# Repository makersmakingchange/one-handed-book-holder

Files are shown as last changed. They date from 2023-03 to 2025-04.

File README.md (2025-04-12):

<!--  Open Source Assistive Technology: GitHub Readme Template -->
<!-- Template files available at https://github.com/makersmakingchange/OpenAT-Template -->

<!-- TITLE -->
# One Handed Book Holder

<!-- SUMMARY -->
The One Handed Book Holder is an inexpensive 3D printed device that makes it easier to hold the pages of a book open with only one hand. Users with limited hand dexterity or use of only one hand my find this device beneficial.  

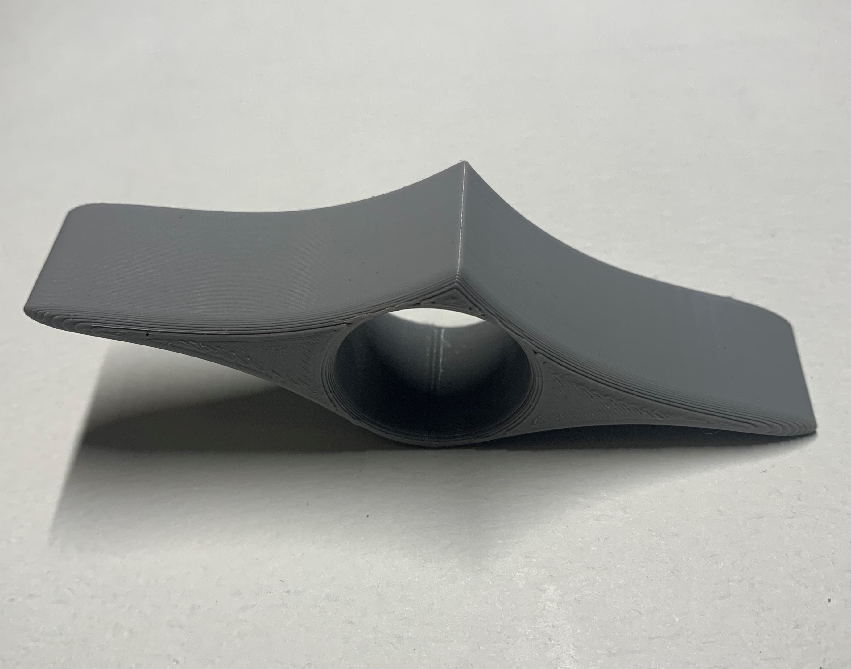
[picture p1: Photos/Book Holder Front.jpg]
The front view of a grey 3D printed handheld book holder


## Makers Making Change Assistive Device Library
 - https://www.makersmakingchange.com/s/product/one-handed-book-holder/01tJR00000092SPYAY

## How to Obtain a One Handed Book Holder
### 1. Do it Yourself (DIY) or Do it Together (DIT)

This is an open-source assistive technology, so anyone is free to build it. All of the files and instructions required to build a One Handed Book Holder are contained within this repository. Refer to the Maker Checklist below.

### 2. Request a build of this device

If you would like to obtain a One Handed Book Holder, you may submit a build request through the [MMC Library Page](https://makersmakingchange.com/project/one-handed-book-holder/). The requestor is responsible for the cost of materials and any shipping.

### 3. How to build this device for someone else

If you have the skills and equipment to build this device, and would like to donate your time to create this device for someone who needs it, visit the [MMC Maker Wanted](https://makersmakingchange.com/maker-wanted/) section.

## Getting Started

### 1. Print the 3D Printable components

All of the files and individual print files can be in the [/Build_Files/3D_Printing_Files](/Build_Files/3D_Printing_Files/) folder.

## Files
This section includes all the information and files required to build and modify the device, including documentation, design files, and build files. 

### Documentation
<!-- DOCUMENTATION -->
| Document | Version | Link |
|----------|---------|------|
| Design Rationale     | 1.0 | [One_Handed_Book_Holder_Design_Rationale](/Documentation/One_Handed_Book_Holder_Design_Rationale.pdf) |
| Bill of Materials    | 1.0 | [One_Handed_Book_Holder_BOM](/Documentation/One_Handed_Book_Holder_BOM.xlsx) |
| Assembly Guide       | N/A | No Assembly Required
| Maker Checklist      | 1.0 | [One_Handed_Book_Holder_Checklist](/Documentation/One_Handed_Book_Holder_Maker_Checklist.pdf) |
| User Guide           | 1.0 | [One_Handed_Book_Holder](/Documentation/One_Handed_Book_Holder_User_Guide.pdf)           |
| Changelog            | 1.0 | [One_Handed_Book_Holder_Changelog](/Documentation/One_Handed_Book_Holder_Changelog.pdf)               |

### Design Files
<!-- DESIGN FILES -->
- Not available 

### Build Files
<!-- BUILD FILES -->
 - [3D Printing Files](/Build_Files/3D_Printing_Files)

## License
<!-- LICENSE -->
Everything needed or used to design, make, test, or prepare the One Handed Book Holder is licensed under the CERN 2.0 Permissive license <https://ohwr.org/project/cernohl/wikis/Documents/CERN-OHL-version-2> (CERN-OHL-P).

Accompanying material such as instruction manuals, videos, and other copyrightable works that are useful but not necessary to design, make, test, or prepare the One Handed Book Holder are published under a Creative Commons Attribution-ShareAlike 4.0 license <https://creativecommons.org/licenses/by-sa/4.0/> (CC BY-SA 4.0).

## Attribution
<!-- ATTRIBUTION -->
 - Design by [Mathis](https://www.myminifactory.com/users/mgigli) and posted on [MyMiniFactory](https://www.myminifactory.com/object/3d-print-one-hand-book-holder-41414)
 - Documentation by Makers Making Change
 - The documentation template was created by Makers Making Change and is used under a CC BY-SA 4.0 license. It is available at the following link: https://github.com/makersmakingchange/OpenAT-Template

----

<!-- ABOUT MMC START -->
## About Makers Making Change
[Makers Making Change Logo](https://www.makersmakingchange.com/)

Makers Making Change is a program of [Neil Squire](https://www.neilsquire.ca/), a Canadian non-profit that uses technology, knowledge, and passion to empower people with disabilities.

Makers Making Change leverages the capacity of community based Makers, Disability Professionals and Volunteers to develop and deliver affordable Open Source Assistive Technologies.

 - Website: [www.MakersMakingChange.com](https://www.makersmakingchange.com/)
 - GitHub: [makersmakingchange](https://github.com/makersmakingchange)
 - Bluesky: [@makersmakingchange.bsky.social](https://bsky.app/profile/makersmakingchange.bsky.social)
 - Instagram: [@makersmakingchange](https://www.instagram.com/makersmakingchange)
 - Facebook: [makersmakechange](https://www.facebook.com/makersmakechange)
 - LinkedIn: [Neil Squire Society](https://www.linkedin.com/company/neil-squire-society/)
 - Thingiverse: [makersmakingchange](https://www.thingiverse.com/makersmakingchange/about)
 - Printables: [MakersMakingChange](https://www.printables.com/@MakersMakingChange)

### Contact Us
For technical questions, to get involved, or to share your experience we encourage you to [visit our website](https://www.makersmakingchange.com/) or [contact us](https://www.makersmakingchange.com/s/contact).
<!-- ABOUT MMC END -->

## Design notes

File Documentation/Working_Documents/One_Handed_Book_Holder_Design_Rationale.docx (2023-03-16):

# Introduction

The One Handed Book Holder is an inexpensive 3D printed device that makes it easier to hold the pages of a book open with only one hand. Users with limited hand dexterity or use of only one hand my find this device beneficial.

# Research

## Commercial Designs

Title | Picture | Cost | Notes:

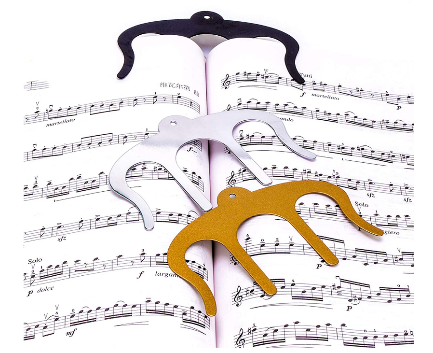
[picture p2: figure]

Music Book Clip (https://www.amazon.ca/Music-Book-Clips-Metal-Holders-Reading/dp/B07TCGN5NL?cv_ct_cx=page+holder&sbo=RZvfv%2F%2FHxDF%2BO5021pAnSA%3D%3D) | | $10 - $20 | This clip can be placed between the pages of a book to keep it open while reading. Typically used for sheet music, cooking books or other books are held on the same page for extended periods of time.

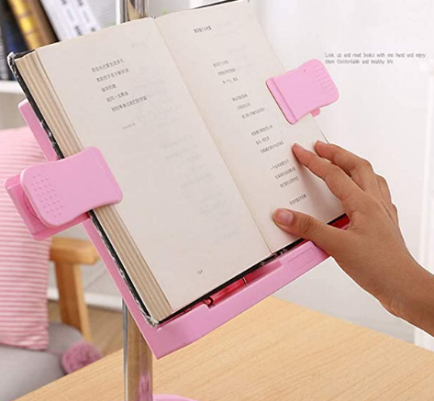
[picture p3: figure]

Adjustable Book Holder (https://www.amazon.ca/Adjustable-Multi-Function-One-Handed-Childrens-Artifact/dp/B08NYQLSL6) | | ~$80 | A stand that holds the pages of a book open with clips on either side. Reading height and angle can be adjusted.

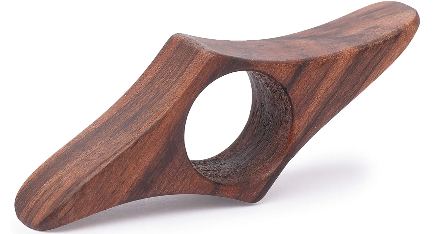
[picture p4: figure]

Book Page Holder (https://www.amazon.ca/TILISMA-Book-Page-Holder-Accessories/dp/B07PGW7C8R?cv_ct_cx=page+holder&sbo=RZvfv%2F%2FHxDF%2BO5021pAnSA%3D%3D) | | $10 - $20 | This device is placed on the user’s thumb to spread apart the pages of a book while actively reading. As it’s not fastened to the book, pages can still be turned easily.

DIY Designs

Title | Picture | Designer

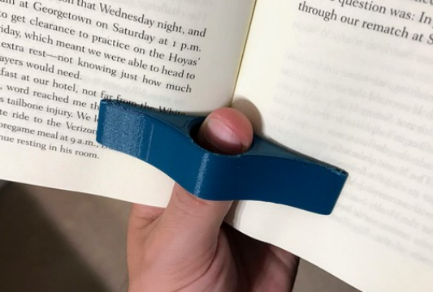
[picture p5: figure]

One Handed Book Holder (https://www.myminifactory.com/object/3d-print-one-hand-book-holder-41414) (Test 1) | | Mathis (https://www.myminifactory.com/users/mgigli)

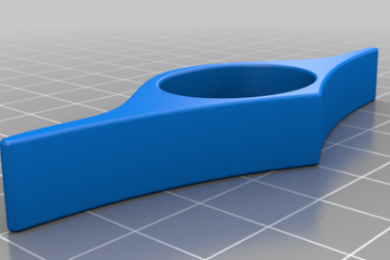
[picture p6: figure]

Page Holder (https://www.thingiverse.com/thing:4832820) (Test 2) | | Myles Kreling (https://www.thingiverse.com/Bison_Soldier)

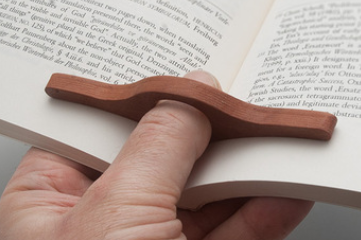
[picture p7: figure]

One Hand Book Holder (https://www.thingiverse.com/thing:2105202) (Test 3) | | Daniel Gross (https://www.thingiverse.com/ZenziWerken)

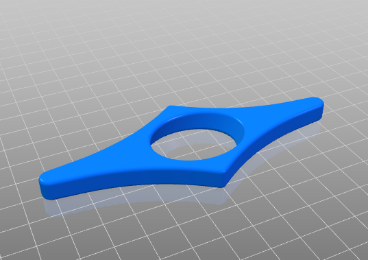
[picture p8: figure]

One Hand Book Holder V2 (https://www.thingiverse.com/thing:5257064) (Test 4) | | Peter Lunk (https://www.thingiverse.com/MrLunk)

# Requirements

## Goals

G01 | Must make it easier for users to hold a book open with one hand.
G02 | Must work or have options for right- and left-handed users.

## Functional Requirements

F01 | Must work for any standard sized book.
F02 | Must not damage or markup the pages of the book.
F03 | Must be comfortable for the user to use.

## Non-functional Requirement

NF01 | Should not require supports.

## Constraints

C01 | Must be printable using PLA
C02 | Must be printable using standard Maker 3D printers

# Existing Device Testing

## Test 1 – One Handed Book Holder (https://www.myminifactory.com/object/3d-print-one-hand-book-holder-41414)

License: MyMiniFactory - Credit - Remix - Noncommercial (https://www.myminifactory.com/object-licensing)

Mass: 7g

Print Time: 1h

### Print Testing

- Must be rotated 90o to print flat.

Initial Print:

- Did not print well
  - Fileted edges on the “arms” didn’t print too well.
  - Area around the thumb hole didn’t adhere to the print bed.

Second Print:

- Added adhesion brim.
- Printed very well and smooth.

### Functional Testing

- Fit nicely on the thumb.
- Good control over its position
- Did not mark the paper.
- Effective at holding the book pages open.

### Summary

This device worked very well when the print settings were adjusted. It effectively held the pages open and did not mark up the paper. It was the thickest holder considered which gave additional control over its position on the page.

## Test 2 – Page Holder (https://www.thingiverse.com/thing:4832820)

License: Attribution 4.0 International (CC BY 4.0)

Mass: 4g

Print Time: 30m

### Print Testing

- Printed very well.
- Surfaces are smooth.
- No supports or additional settings.

### Functional Testing

- Fit very nicely on the thumb.
- Easy to position.
- Arms were on the short side.
- Left marks on the page.

### Summary

This was the only device that had an oval thumb hole, making it fit and feel very nice. This also gave additional control over the positioning of the holder. However, it’s arms were quite short and had minimal rounding where they contacted the pages. This caused the device to leave marks on the paper.

## Test 3 – One Hand Book Holder (https://www.thingiverse.com/thing:2105202)

License: Attribution-NonCommercial-ShareAlike 4.0 International (CC BY-NC-SA 4.0)

Mass: 5g

Print Time: 38m

### Print Testing

- Printed very well.
- No supports or additional settings.

### Functional Testing

- Thumb hole is very small.
- Has long arms allowing It to effectively hold open the pages.
- No rounding making it uncomfortable and left marks on the paper.

### Summary

The original design was intended to laser cut out of wood. The thumb hole was quite small and the lack of edge rounding made it uncomfortable and left marks on the pages.

## Test 4 – One Hand Book Holder V2 (https://www.thingiverse.com/thing:5257064)

License: Attribution 4.0 International (CC BY 4.0)

Mass: 6g

Print Time: 44m

### Print Testing

- Printed very well.
- No supports of additional settings.

### Functional Testing

- Angled thumb hole so thumb can rest more naturally while reading.
- Thumb hole too large.
- Very hard to control and position.

### Summary

A few commons left on various other designs had requested an angled thumb hole to allow for an alternative grab. However, this large, angled thumb hole along with it being the thinnest considered, made this design very difficult to position on the page.

# Device Selection

Of the 4 designs considered, only the first one tested (Test 1 - One Handed Book Holder (https://www.myminifactory.com/object/3d-print-one-hand-book-holder-41414)) met every design requirement. After making some simple adjustments to the print orientation and settings, it effectively printed, felt comfortable to use, successfully held pages open and left no marks on the paper. For these reasons, we will proceed using this design for the final device.

# Opportunities for Improvement

- Adjustments to the fillets on the arms to increase the quality of the print.
- Refine the thickness of design to allow for adequate control while not covering too much of the page.

© 2023 by Neil Squire This work is licensed under the CC BY SA 4.0 License: http://creativecommons.org/licenses/by-sa/4.0 Files available at https://makersmakingchange.com/project/one-handed-book-holder Page 1 of 1

V1.0 | March 2023 One Handed Book Holder Design Rationale

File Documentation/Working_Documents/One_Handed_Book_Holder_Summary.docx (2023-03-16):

# Title

One Handed Book Holder

## Subtitle

An inexpensive 3D printed device that makes it easier to hold open a book.

## Device Specifications

Build Time:

< 1hr

1-4 hr

5-10hr

>10hr

Cost:

$0 - $10

$11 - $25

$26 - $50

$51 - $100

$101 - $250

$250+

Stage: Recently Added

Skills: 3D Printing

Need: Agility/Dexterity

Disability: Mobility / Physical

Difficulty: Beginner

License:

Usages: ADL, RL

Type:

Designer: Mathis (https://www.myminifactory.com/users/mgigli)

## Device Details

### Overview

The One Handed Book Holder is an inexpensive 3D printed device that makes it easier to hold the pages of a book open with only one hand. Users with limited hand dexterity or use of only one hand my find this device beneficial.

### Usage

To use this device, inset a thumb or finger into the finger hole. Slide the device between two pages of a book and rest the “pointed” side in the center crease. The arms of the device will hole the pages open while you read.

### Cost

This cost of filament to print this device is approximately $0.20.

#### Skills Required

This is a beginner level build that requires minimal 3D printing.

### Build Instructions

Refer to the 3D Printing Guide for detailed instructions.

#### Time Required

3D Printing Time: ~60min

Assembly Time: No assembly required.

#### Tools

- 3D Printer
- Fine grit sandpaper (Optional)

#### 3D Printing

1X One_Handed_Book_Holder.stl

### Attribution

Design by Mathis (https://www.myminifactory.com/users/mgigli) and posted on MyMiniFactory (https://www.myminifactory.com/object/3d-print-one-hand-book-holder-41414).

© 2023 by Neil Squire This work is licensed under the CC BY SA 4.0 License: http://creativecommons.org/licenses/by-sa/4.0 Files available at https://makersmakingchange.com/project/one-handed-book-holder Page 1 of 1

V1.0 | March 2023 One Handed Book Holder Summary

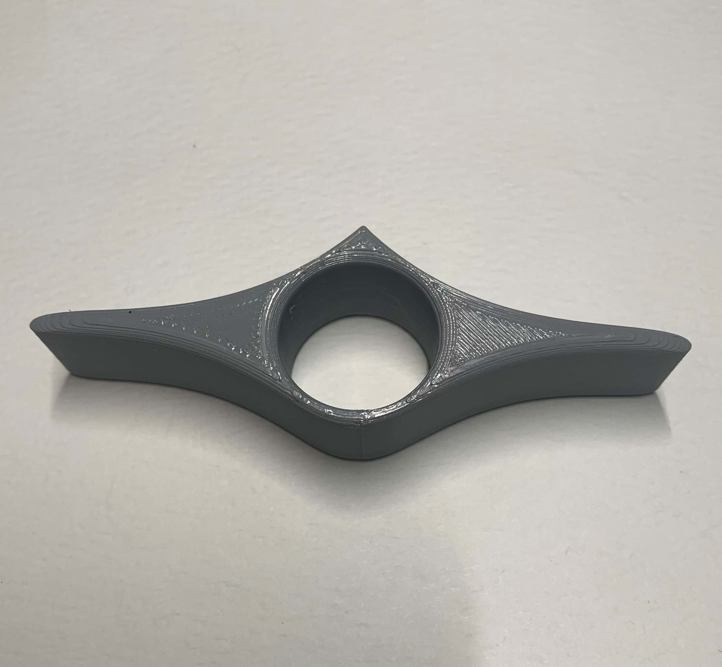
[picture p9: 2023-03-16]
Photos/Book Holder Top.jpg

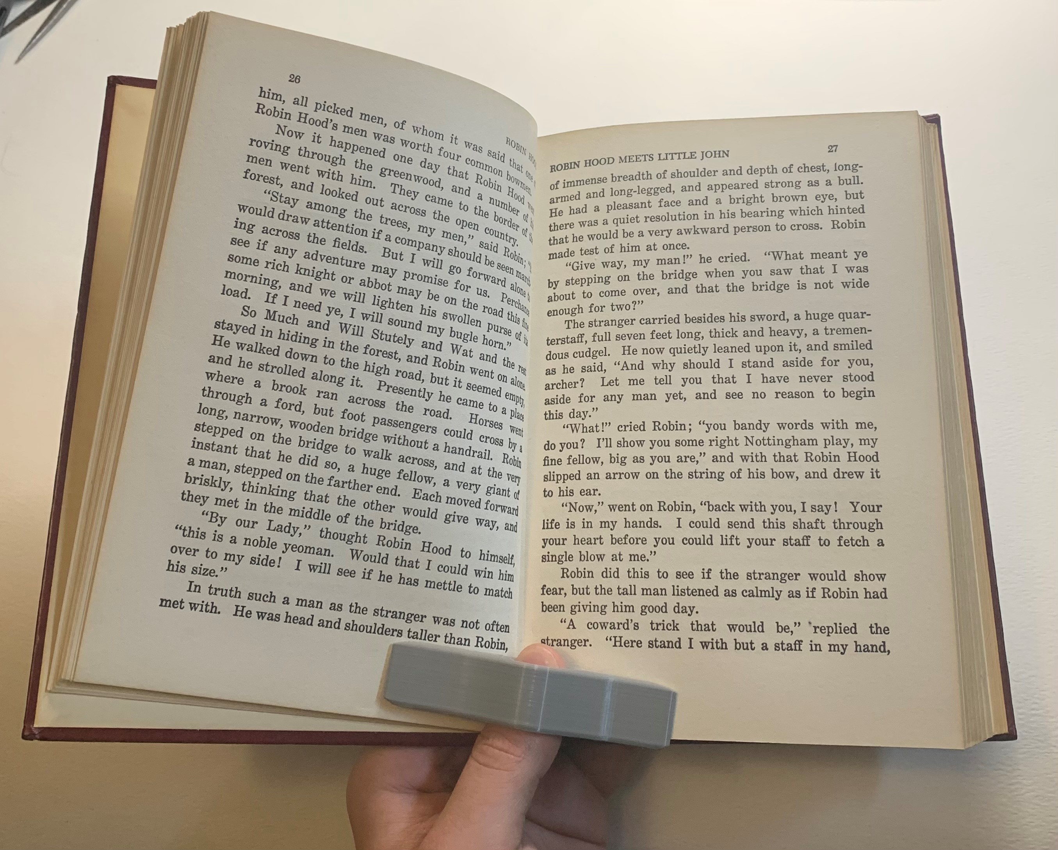
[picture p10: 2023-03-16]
Photos/Book Holder in use.jpg

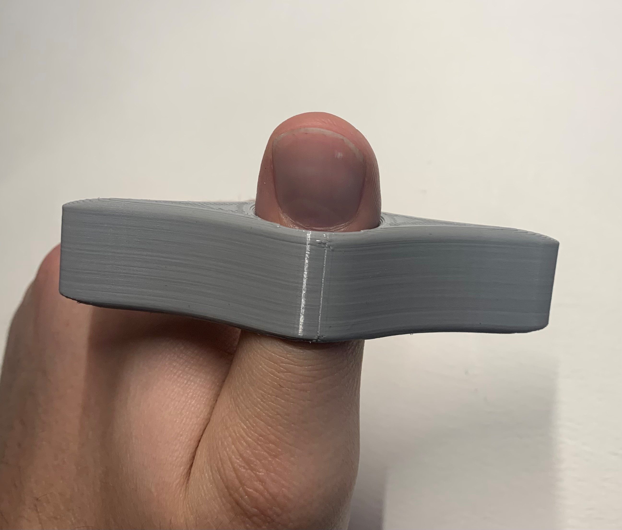
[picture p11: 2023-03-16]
Photos/Book Holder on thumb.jpg

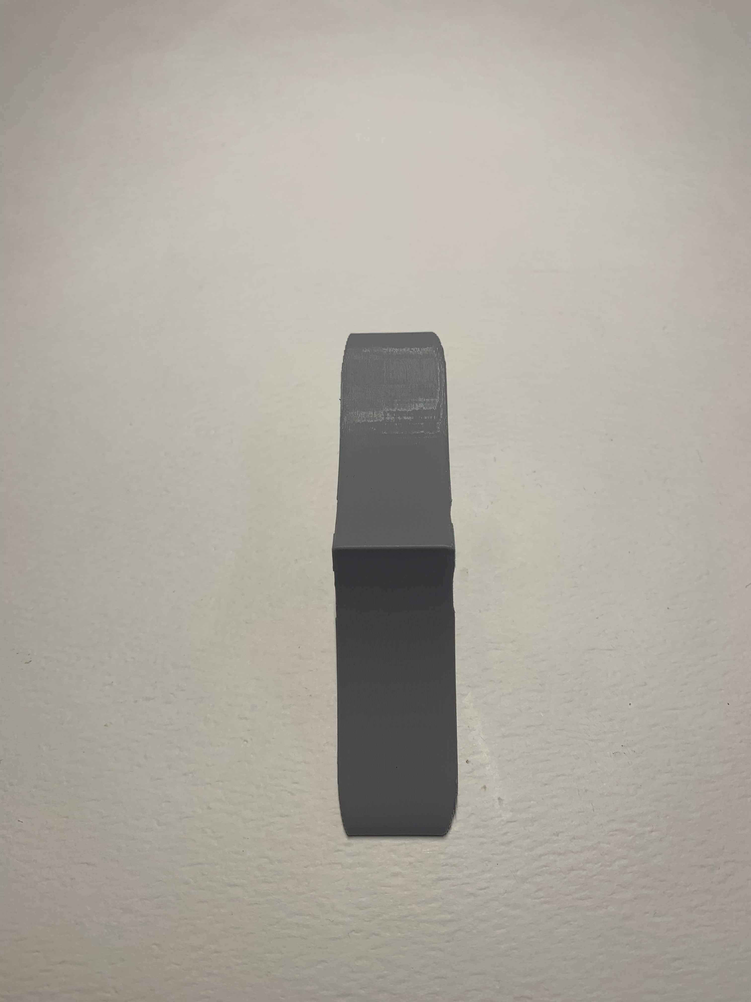
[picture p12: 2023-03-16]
Photos/Book Holder Side.jpg

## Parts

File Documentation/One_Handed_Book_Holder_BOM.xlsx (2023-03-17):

One Handed Book Holder |  |  |  |  |  |  |  | Unit Cost | Total Cost | Total Print time (hr) | Total filament (g)
Version: V1.0 |  | Last Updated: 2023-March-16 |  |  |  |  |  | $0.18 | $0.18 | 1.00 | 7
Commercial Parts
ID | Part Name | Part Type | QTY | QTY/PKG | $/PKG | PKG QTY | $/Unit | Extended | Total | Link
 | Not Required.
3D Printed Parts ESTIMATED PRICING USING 1KG ROLL COST: |  | $25.00
ID | Part | Material | QTY | Mass (g) / Unit | Time / Unit |  | Print Time (Min) | Estimated Price |  | Link
 | One Handed Book Holder | PLA | 1 | 7 | 60 |  | 60 | $0.18 |  | 3D Printable One hand book holder by Mathis (myminifactory.com) (https://www.myminifactory.com/object/3d-print-one-hand-book-holder-41414)
Custom Printed Circuit Board (PCB)
ID | Part |  | QTY
 | Not Required.
Tools for Assembly
 | Sand Paper (Optional)
Alternatives (if there are other sources for some parts link them below)
ID | Part and description |  |  |  |  |  |  |  |  | Link
 | https://www.thingiverse.com/thing:3004390/files

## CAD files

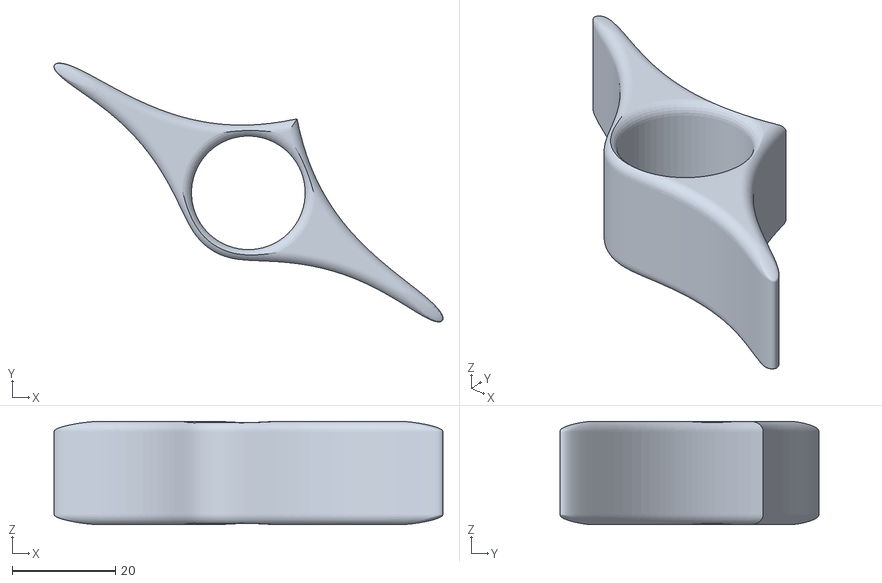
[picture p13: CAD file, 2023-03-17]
Build_Files/3D_Printing_Files/One_Handed_Book_Holder.stl
75.4 x 50.2 x 20.0

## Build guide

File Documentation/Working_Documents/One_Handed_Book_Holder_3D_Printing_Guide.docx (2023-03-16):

# 3D Printing Summary

Configuration | Total Print Time (min) | Total Number of Components | Typical Total Mass (g) | Typical Number of Print Setups
One Handed Book Holder | 60 | 1 | 7 | 1

# 3D Printing Settings

Print File Name | Qty | Total Print Time (hr:min) | Mass (g) | Infill (%) | Support (Y/N) | Layer Height/ Nozzle Diameter(mm) | Notes (orientation, special settings, etc.)
One_Handed_Book_ Holder.stl | 1 | 1:00 | 7 | 10 | N | 0.2/0.4 | - Print in orientation given in STL -Print with a brim

# Customization Options

The users may request their choice of print colour.

# Post-Processing

Remove the brim and ensure that all surfaces and edges are smooth and non-sharp. Pay close attention to the corners on the arms as this can protentional leave marks on book pages if too sharp. Use fine grit sandpaper, as necessary.

# Examples of Quality Prints

Photos of the One Handed Book Holder

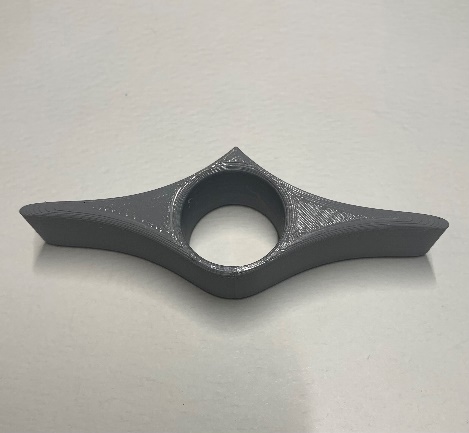
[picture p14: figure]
The top view of a grey 3D printed handheld book holder.
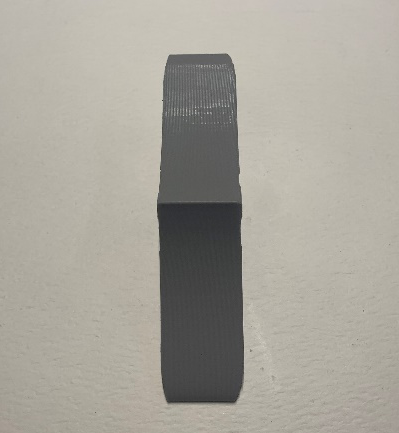
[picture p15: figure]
The side view of a grey 3D printed handheld book holder.

© 2023 by Neil Squire This work is licensed under the CC BY SA 4.0 License: http://creativecommons.org/licenses/by-sa/4.0 Files available at https://makersmakingchange.com/project/one-handed-book-holder Page 1 of 1

V1.0 | March 2023 One Handed Book Holder 3D Printing Guide

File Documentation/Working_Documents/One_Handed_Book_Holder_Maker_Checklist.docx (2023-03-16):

# Maker To Do List

- Read through the Assembly Guide to become familiar with required components, tools, supplies, and safety gear and overall assembly steps.
- Talk to User about customization options (e.g., color, any special requests, etc.)
- Order hardware components
- Gather tools, supplies, and safety equipment.
- Assemble the device
- Test device
- Print “User Guide”

# Items to Give to User

- Assembled, tested device
- “User Guide”

© 2023 by Neil Squire This work is licensed under the CC BY SA 4.0 License: http://creativecommons.org/licenses/by-sa/4.0 Files available at https://makersmakingchange.com/project/one-handed-book-holder Page 1 of 1

V1.0 | March 2023 One Handed Book Holder Maker Checklist

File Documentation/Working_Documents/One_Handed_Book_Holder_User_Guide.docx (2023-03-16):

## Introduction

The One Handed Book Holder is an inexpensive 3D printed device that makes it easier to hold the pages of a book open with only one hand. Users with limited hand dexterity or use of only one hand my find this device beneficial.

## Features

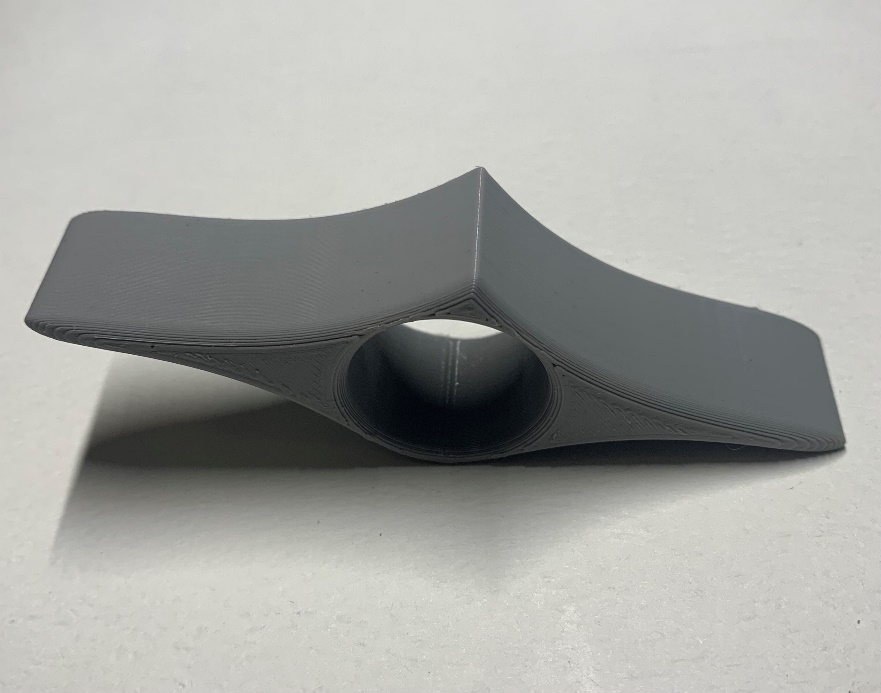
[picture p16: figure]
The front view of a grey 3D printed book holder.

Finger Hole

Page Spreader

## Usage

To use this device, inset a thumb or finger into the finger hole. Slide the device between two pages of a book and rest the “pointed” side in the center crease. The arms of the device will hole the pages open while you read.

## Compatibility

This device can be used to hold open hard and soft cover books of many sizes. The finger hole can accept any thumb or finger less than 21.5 mm in width.

## Specifications

Weight | Length | Width | Thickness | Finger Hole Diameter
~7g | 90mm | 30mm | 20mm | 21.5mm

## Cleaning

To clean this device, use plastic safe cleaning wipes or a damp cloth.

© 2023 by Neil Squire This work is licensed under the CC BY SA 4.0 License: http://creativecommons.org/licenses/by-sa/4.0 Files available at https://makersmakingchange.com/project/one-handed-book-holder Page 1 of 1

V1.0 | March 2023 One Handed Book Holder user Quick Guide

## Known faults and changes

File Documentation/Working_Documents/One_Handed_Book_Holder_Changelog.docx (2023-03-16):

# Version 1.0 | 2023/March/16

- A 3D printed device that makes it easier to hold the pages of a book open.
- Design by Mathis (https://www.myminifactory.com/users/mgigli) and posted on MyMiniFactory (https://www.myminifactory.com/object/3d-print-one-hand-book-holder-41414).
- Licence: MyMiniFactory - Credit - Remix - Noncommercial (https://www.myminifactory.com/object-licensing)
- Documentation by Makers Making Change

© 2023 by Neil Squire This work is licensed under the CC BY SA 4.0 License: http://creativecommons.org/licenses/by-sa/4.0 Files available at https://makersmakingchange.com/project/one-handed-book-holder Page 1 of 1

V1.0 | March 2023 One Handed Book Holder changelog
